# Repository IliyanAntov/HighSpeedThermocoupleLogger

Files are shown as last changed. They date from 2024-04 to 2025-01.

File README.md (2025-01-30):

 <h1 align="center"> Високоскоростен логер за термодвойки с ускорение на измерването<br/><br/>
 High-speed thermocouple logger with measurement acceleration </h1>

## [Документация](./Documentation/DR_Iliyan_Antov_101220020.pdf)

## [Презентация на проекта](./Documentation/Presentation/High%20speed%20thermocouple%20logger.pptx)

## Блокова схема:
<p align="center">
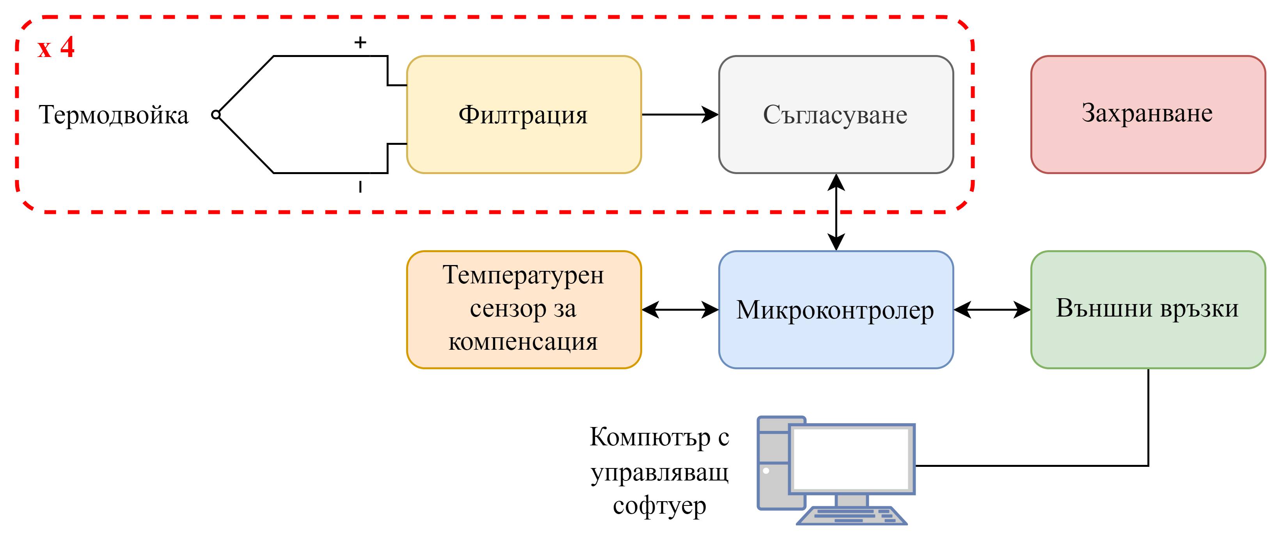
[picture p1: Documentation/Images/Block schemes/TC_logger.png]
  
</p>

## Принципна електрическа схема:
<p align="center" float="left">
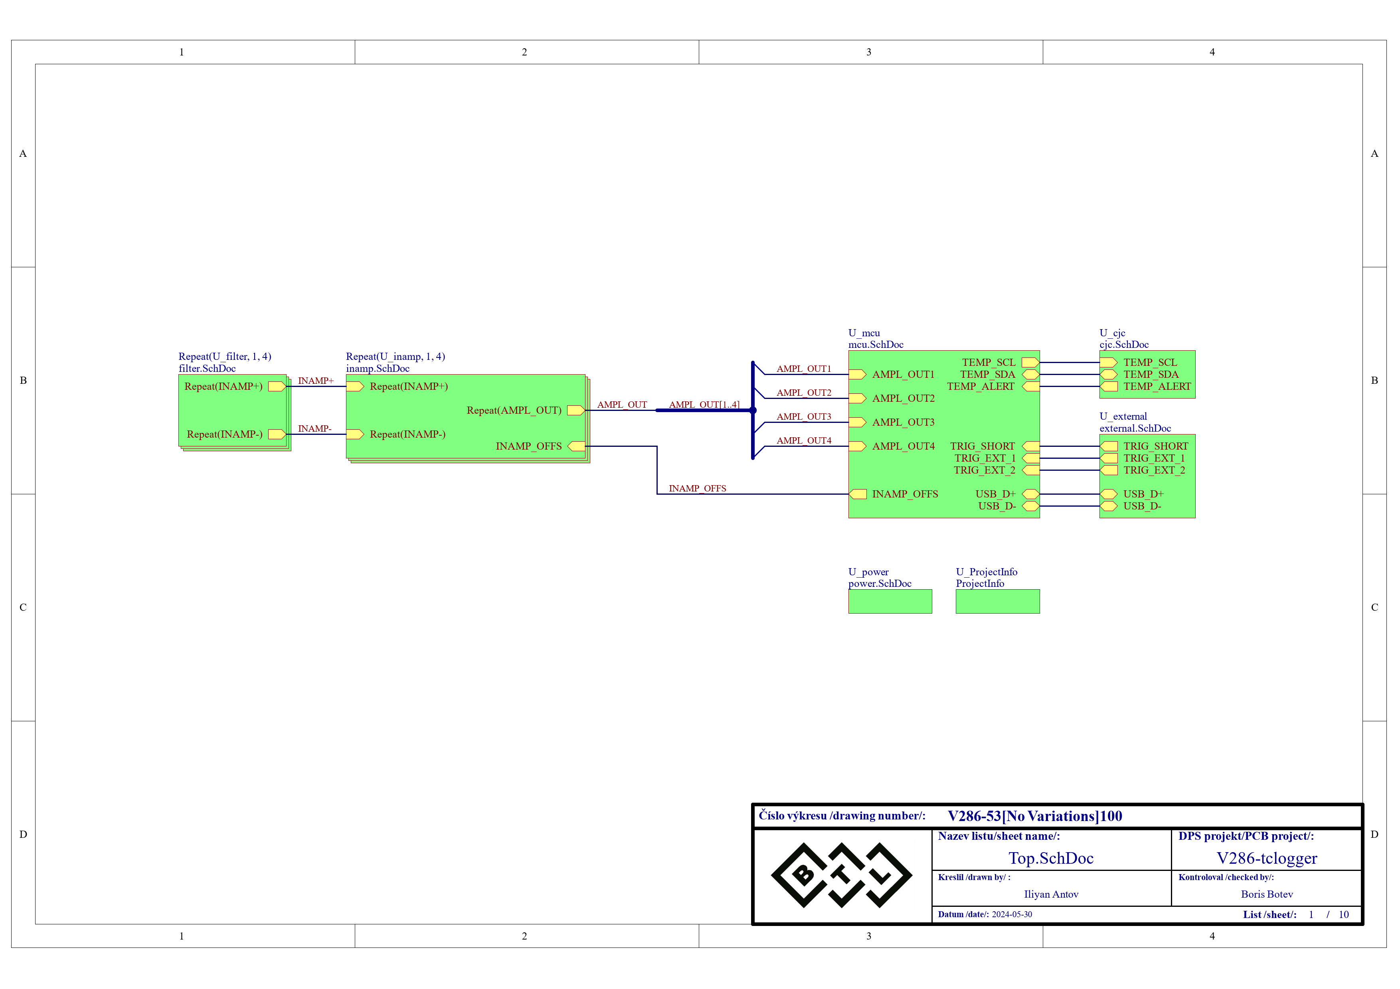
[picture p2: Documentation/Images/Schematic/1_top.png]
  
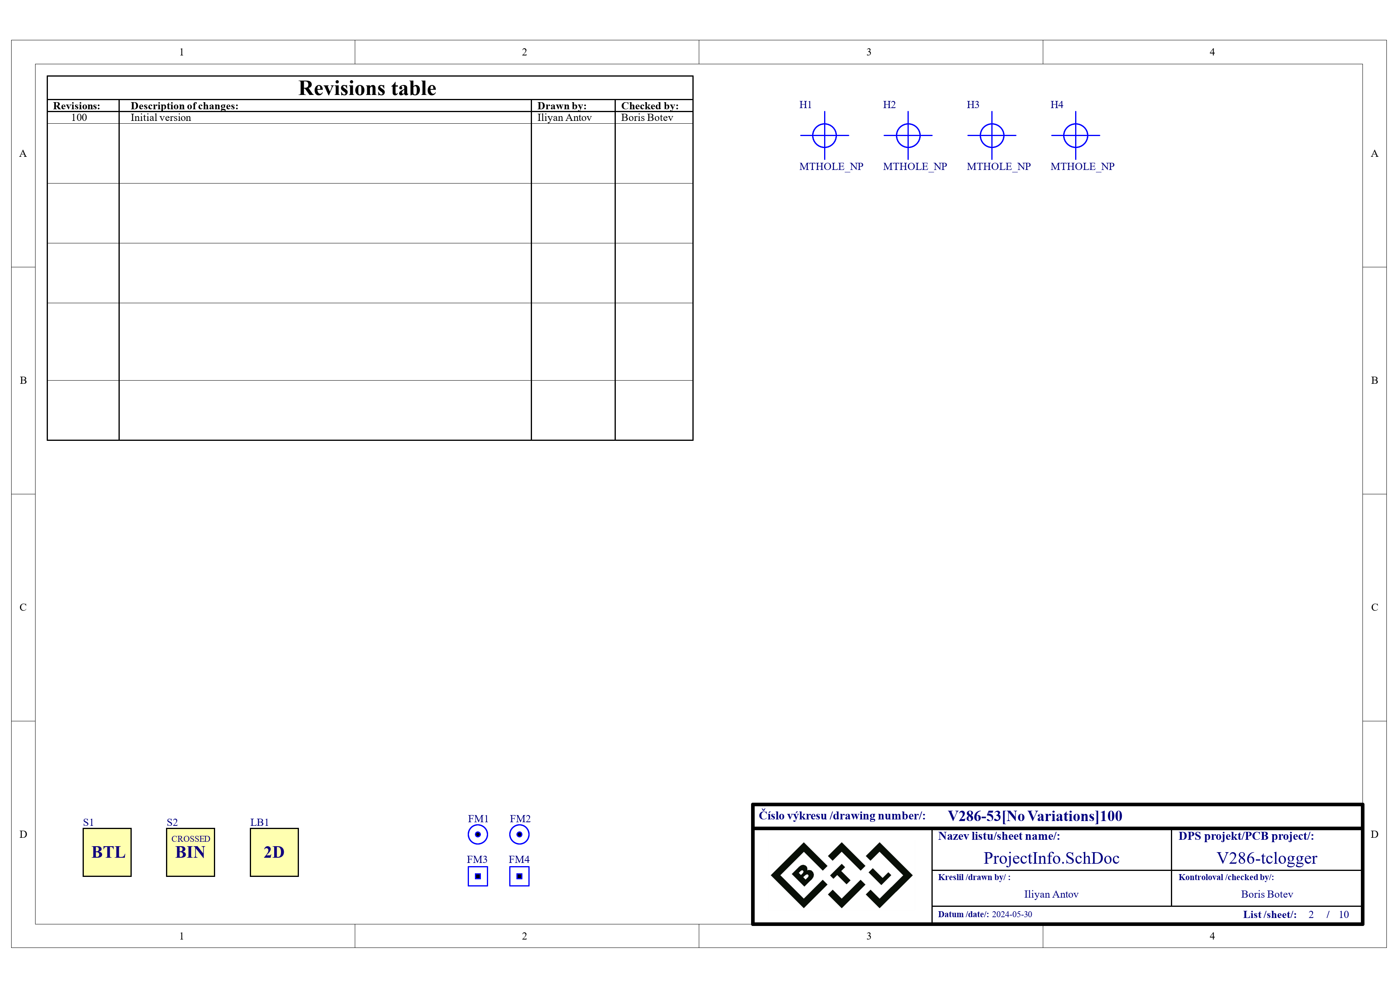
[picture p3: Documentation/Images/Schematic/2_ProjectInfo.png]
  
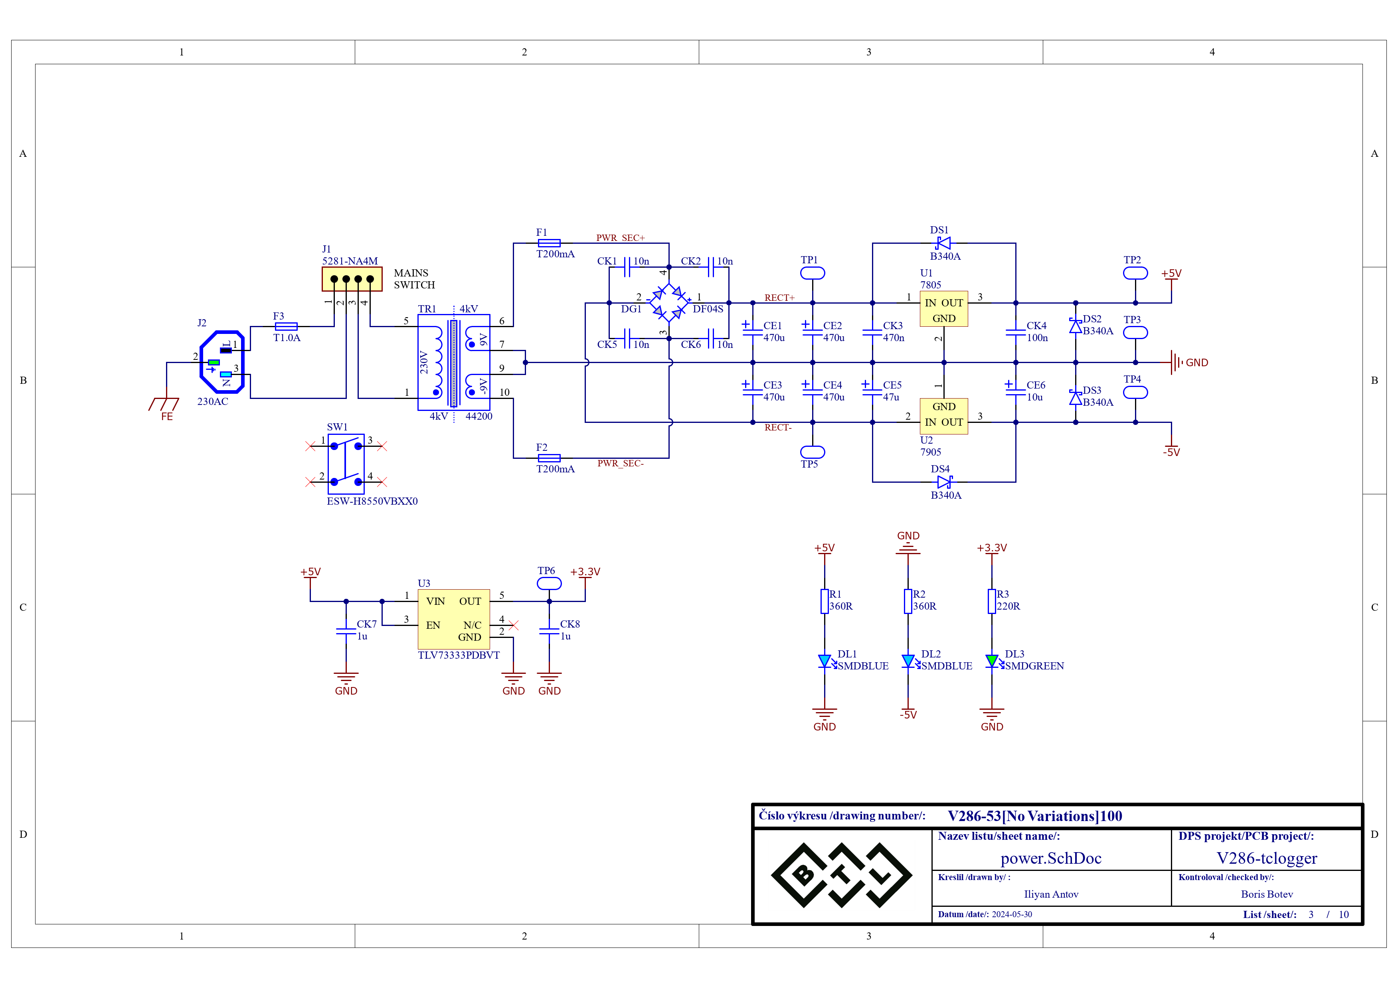
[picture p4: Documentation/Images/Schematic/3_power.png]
  
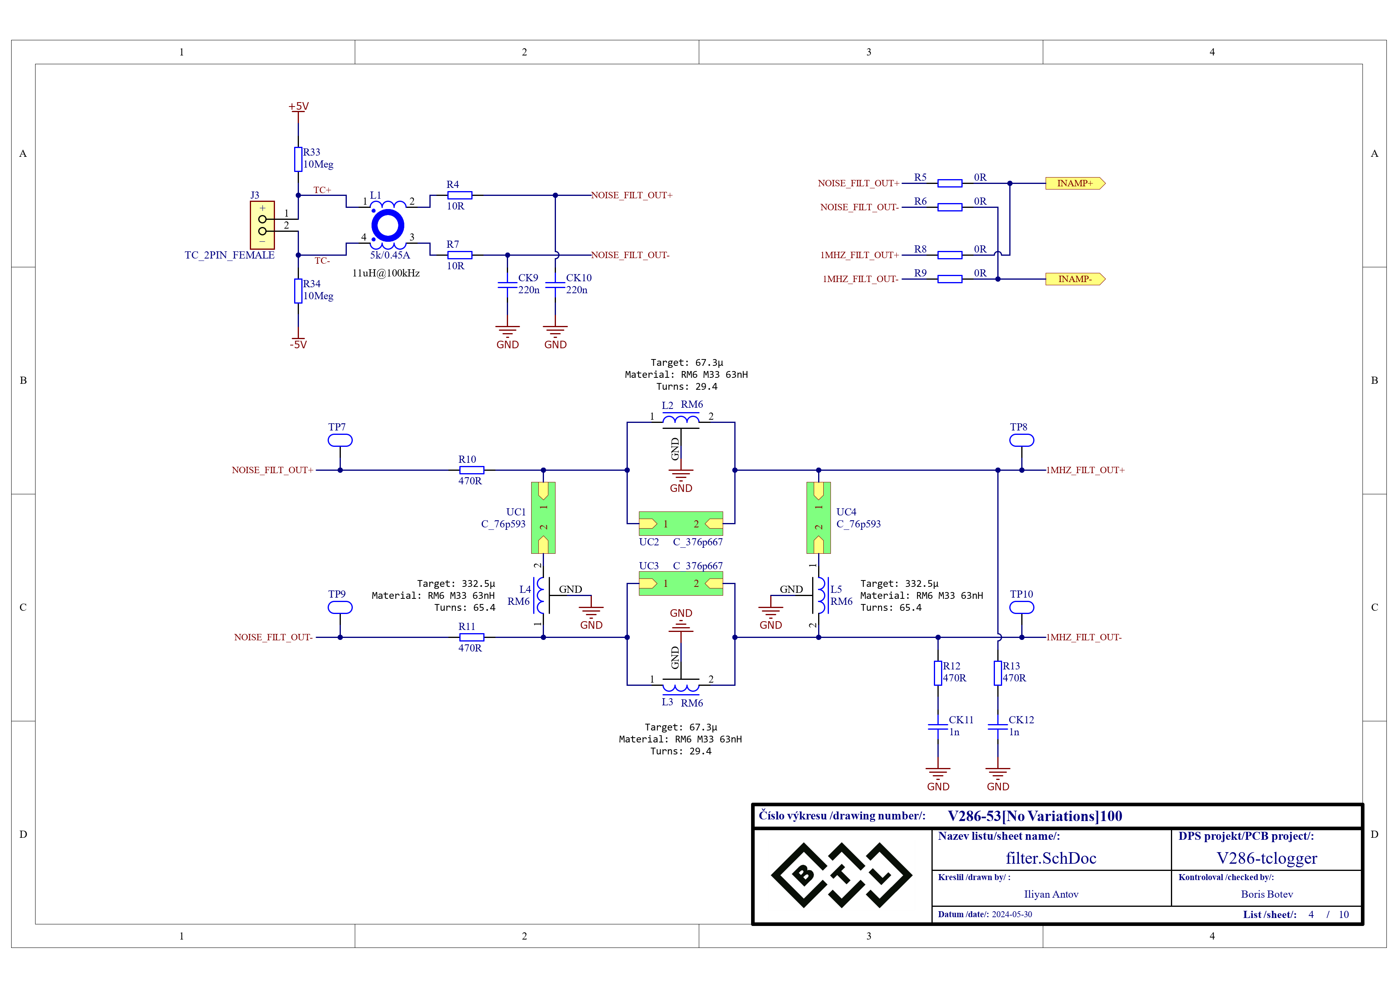
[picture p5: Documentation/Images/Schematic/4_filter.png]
  
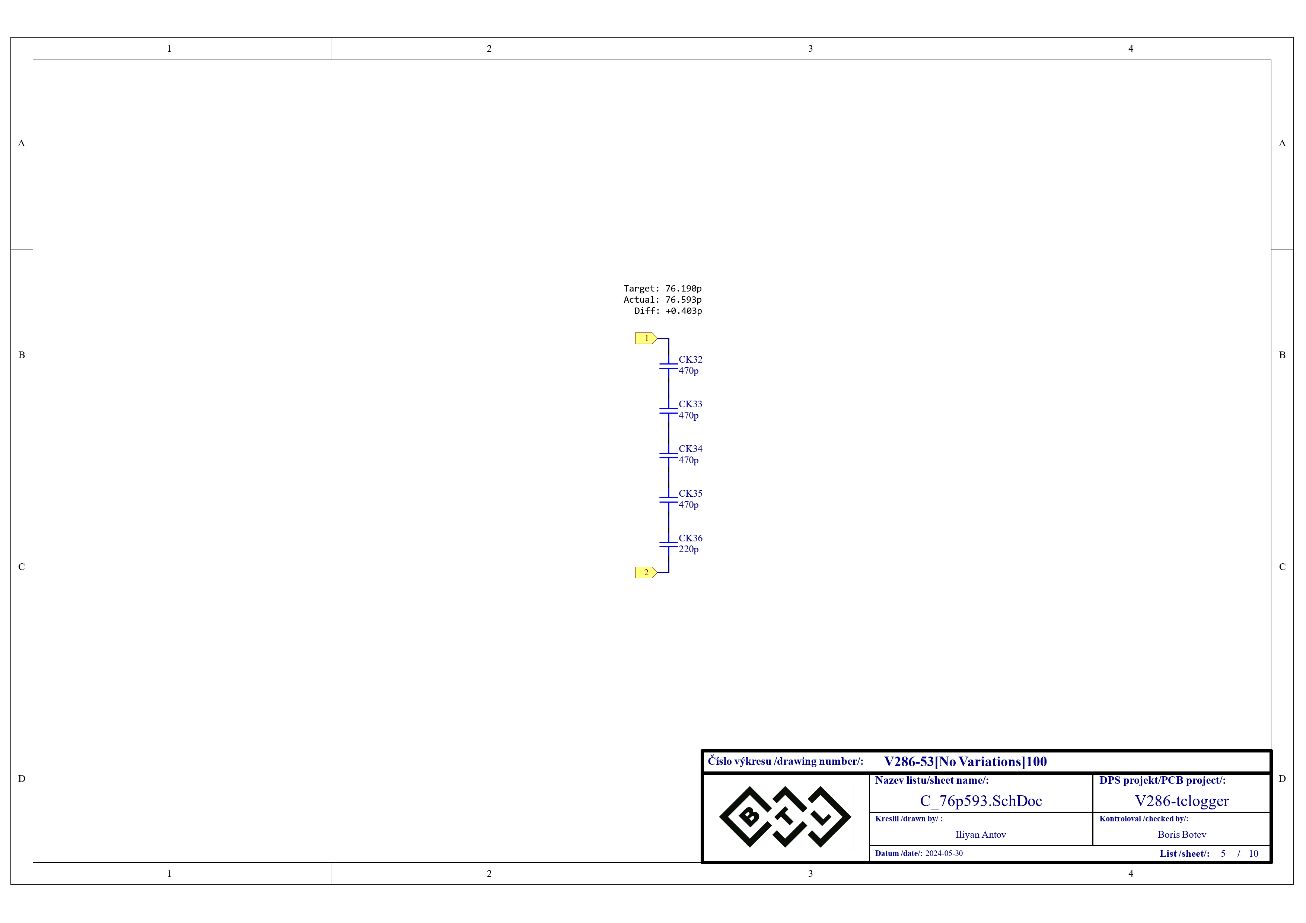
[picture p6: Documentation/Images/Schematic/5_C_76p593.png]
  
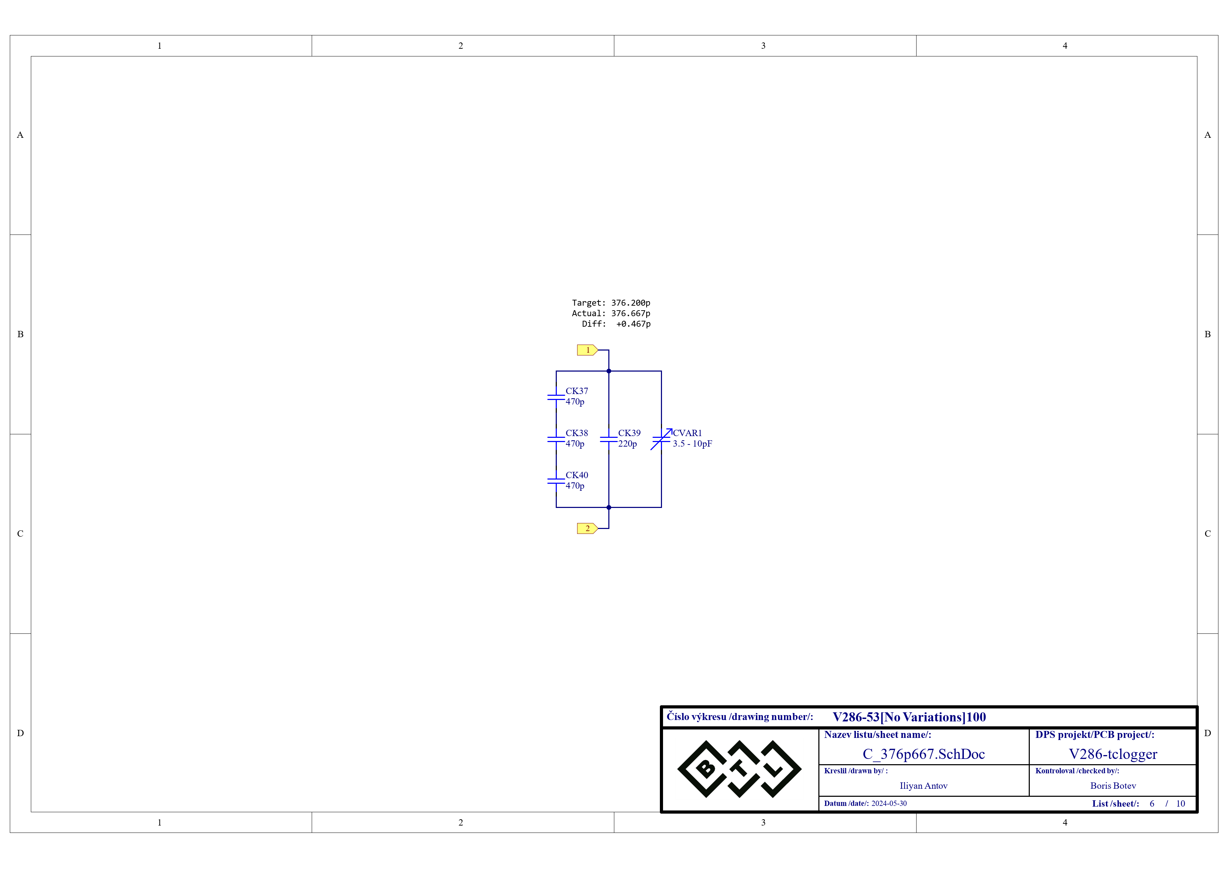
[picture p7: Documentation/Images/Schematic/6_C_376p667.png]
  
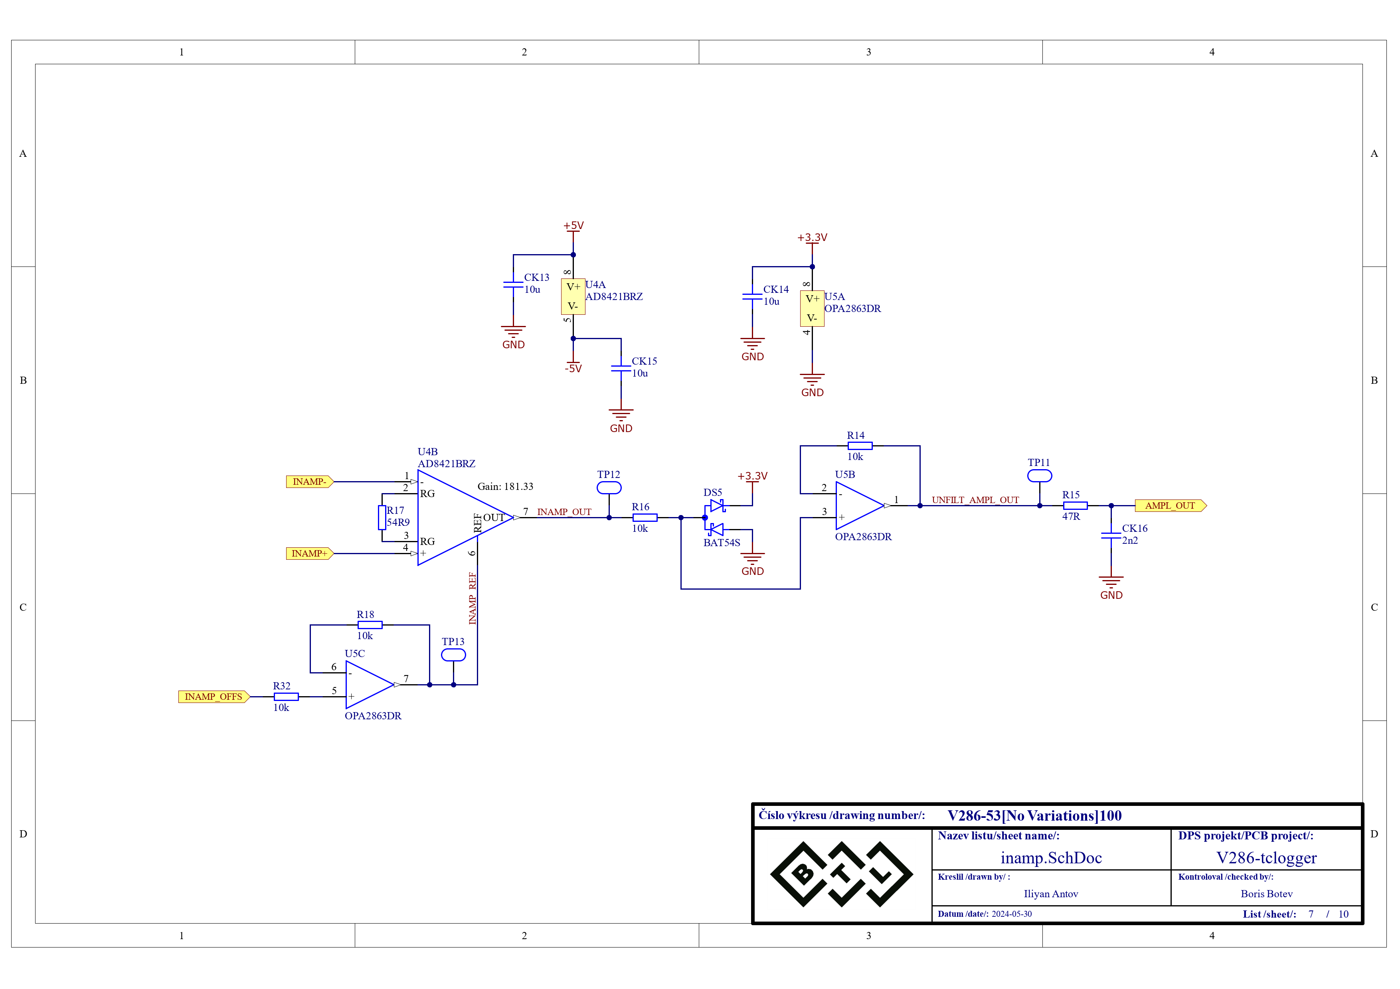
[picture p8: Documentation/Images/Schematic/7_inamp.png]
  
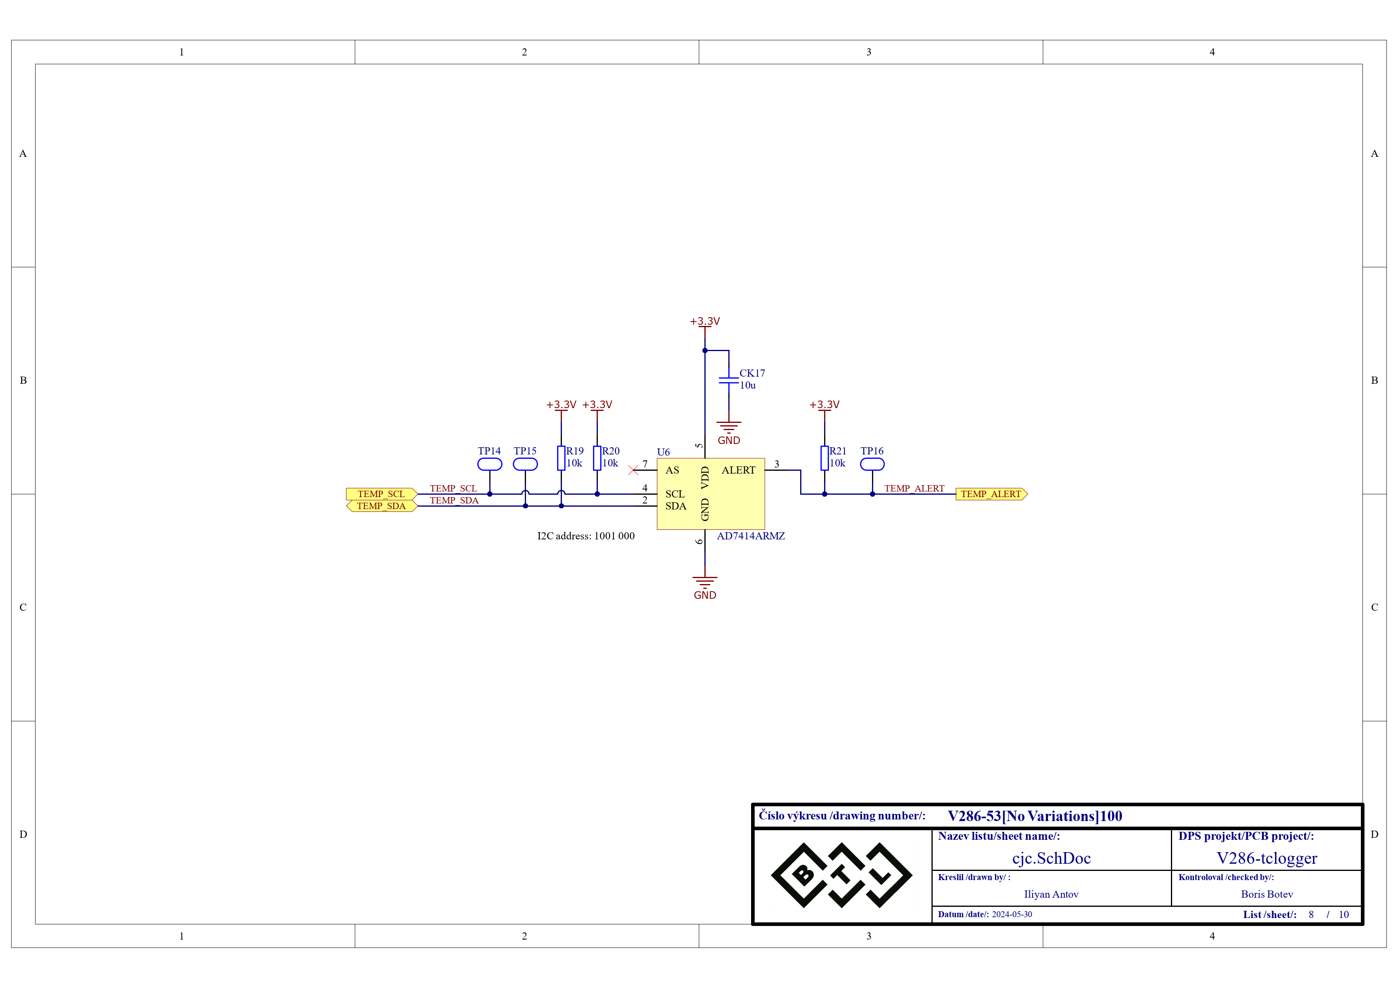
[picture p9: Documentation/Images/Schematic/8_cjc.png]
  
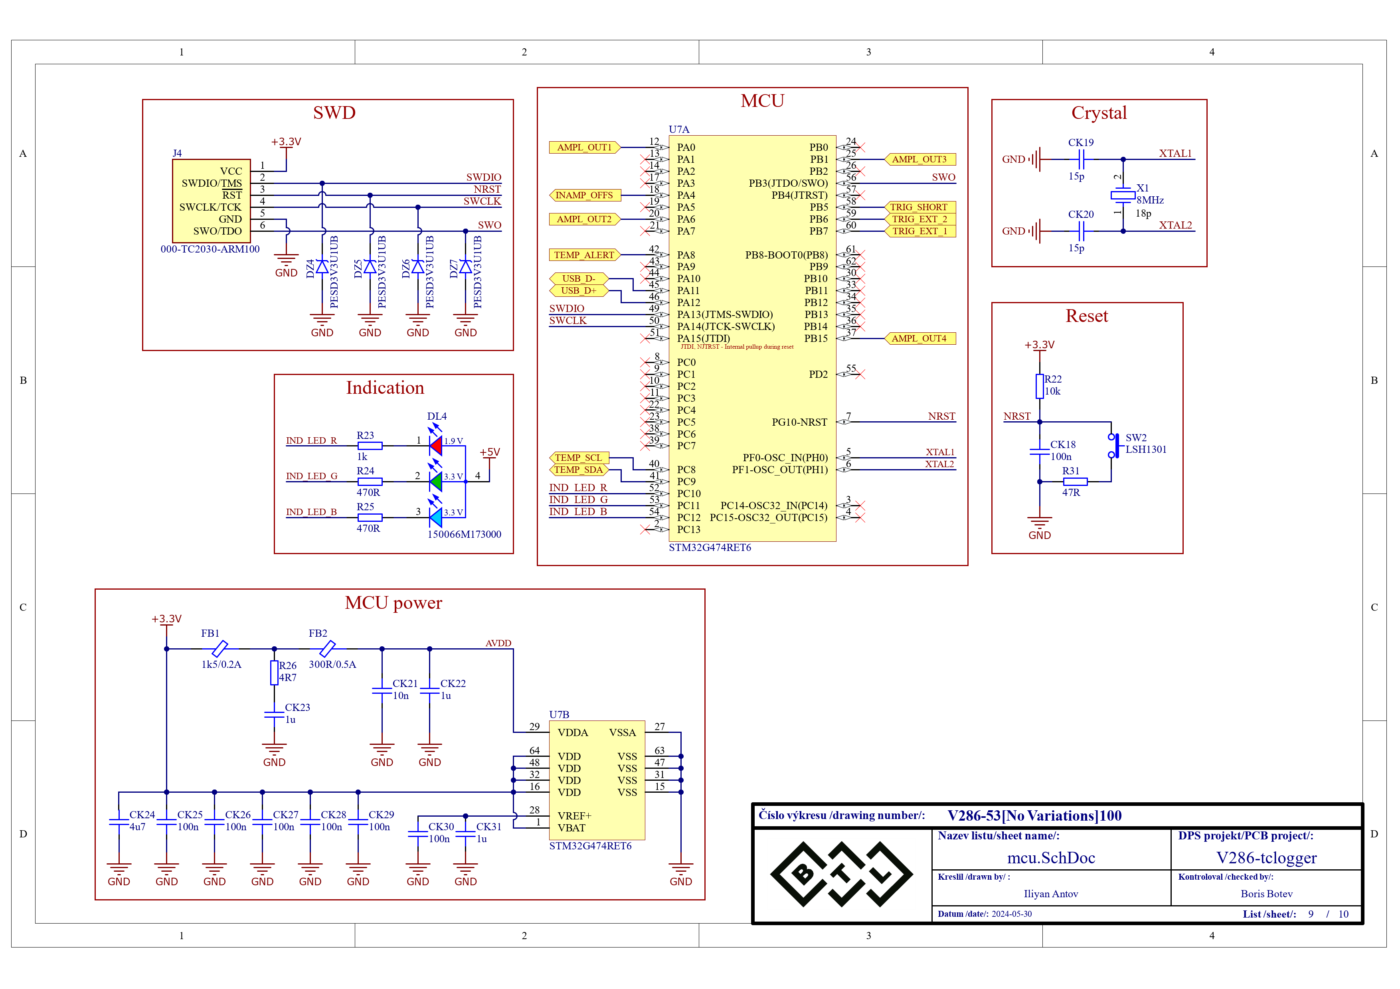
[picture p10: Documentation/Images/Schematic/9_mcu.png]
  
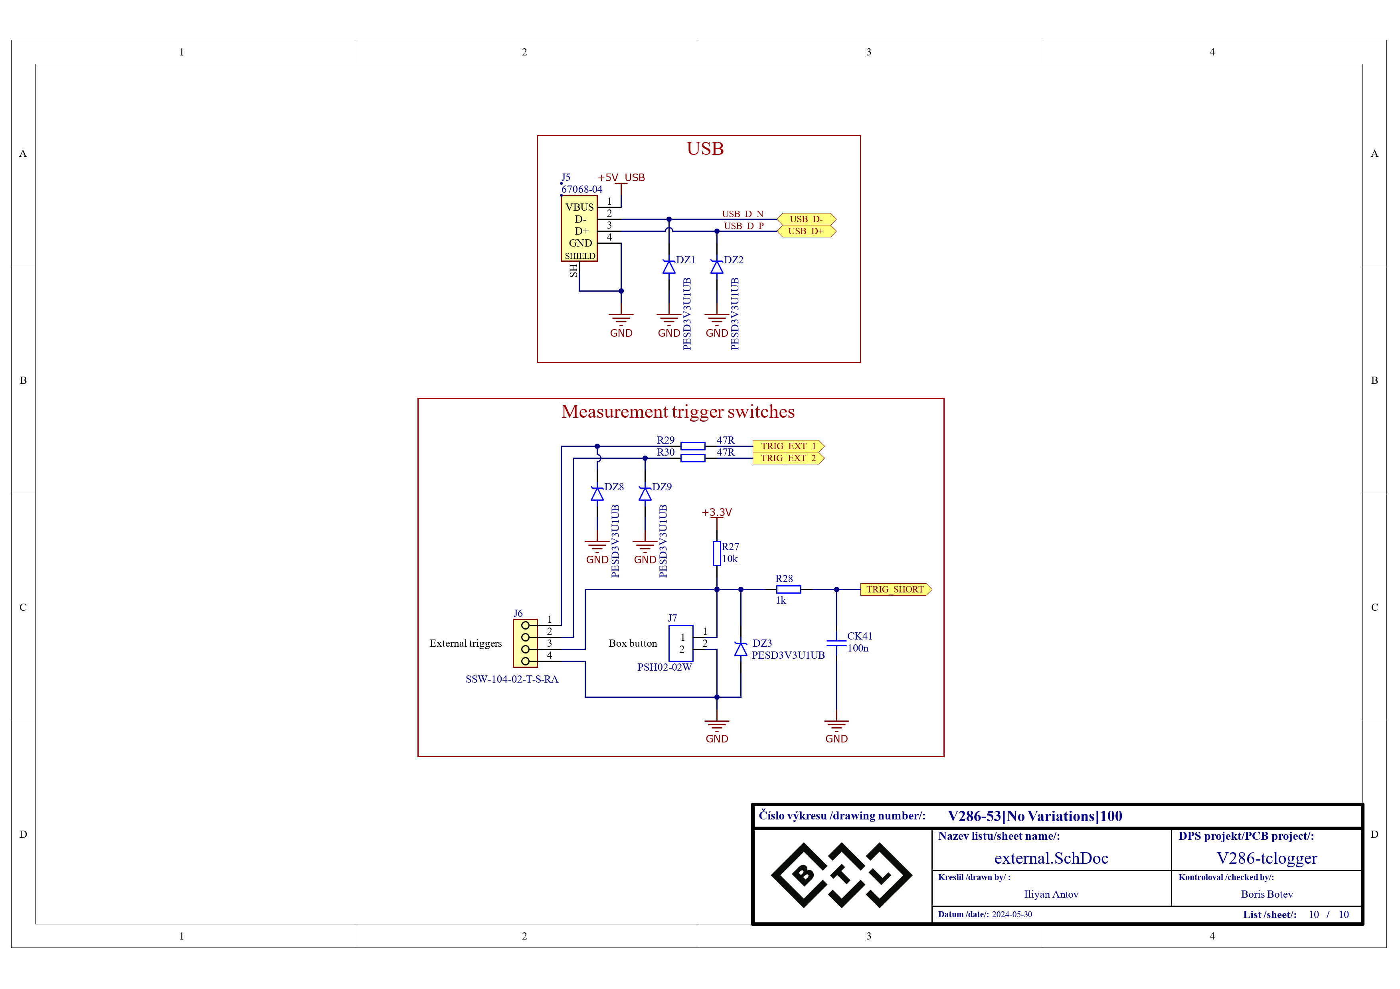
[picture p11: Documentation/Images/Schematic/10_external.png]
  
</p>

## Печатна платка:
<p align="center">
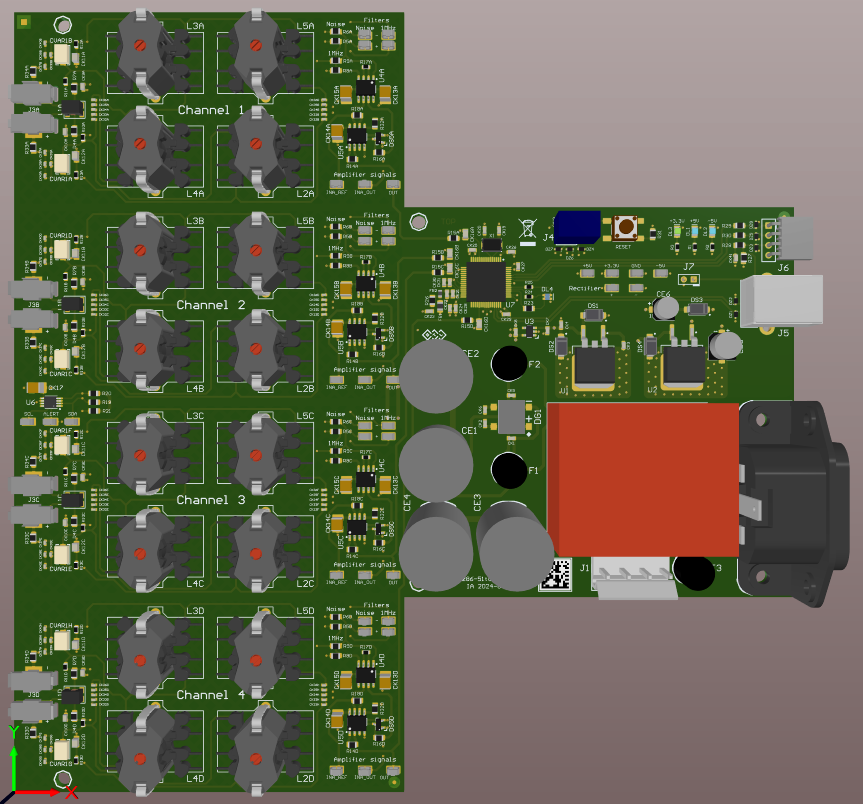
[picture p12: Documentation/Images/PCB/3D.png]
  
</p>

## Реализация:
<p align="center">
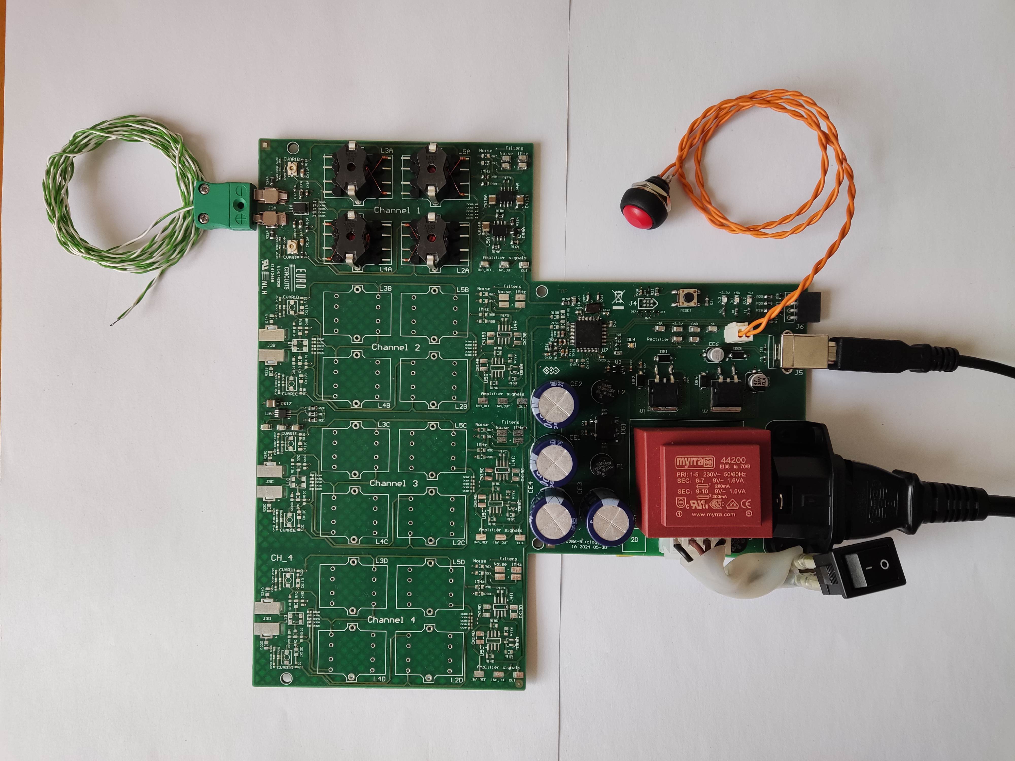
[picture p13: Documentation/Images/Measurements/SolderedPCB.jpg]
  
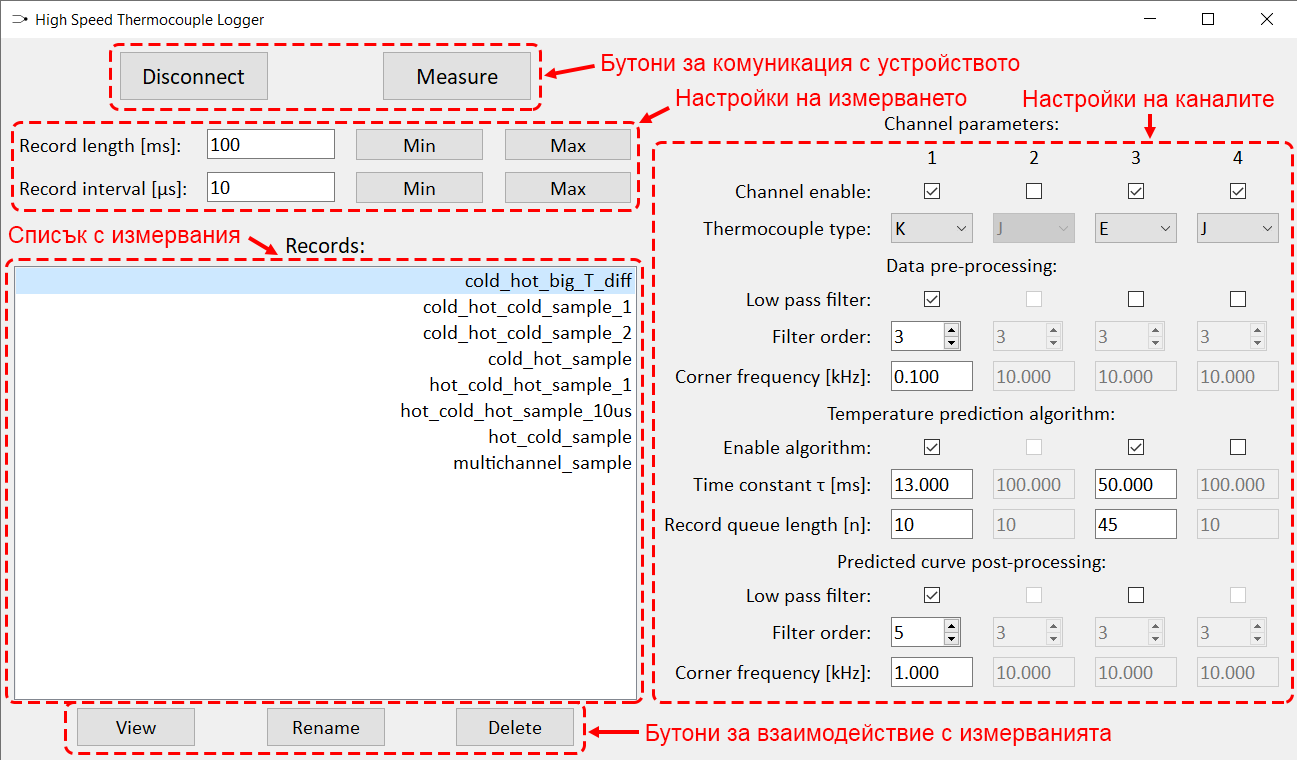
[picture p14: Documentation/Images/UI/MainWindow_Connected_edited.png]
  
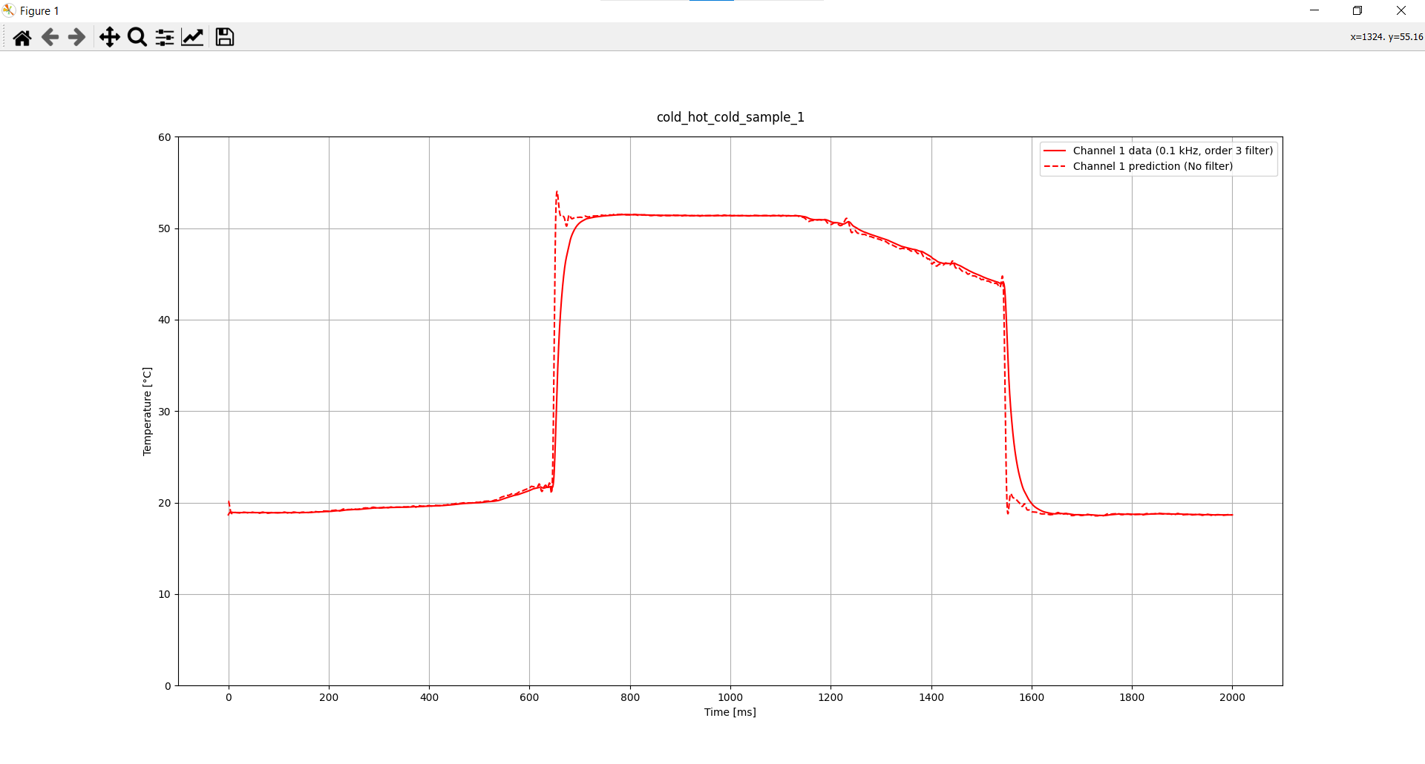
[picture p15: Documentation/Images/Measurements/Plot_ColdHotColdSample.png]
  
</p>

## Използвани технологии:
* PC application: Python + PyQt5
* Firmware: C/C++
* MCU platform: STM32
* Schematics/Layout: Altium

## Автор:
Илиян Антов - [Iliyan Antov](https://github.com/IliyanAntov) - [i.antov2@gmail.com](i.antov2@gmail.com)

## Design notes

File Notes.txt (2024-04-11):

Chosen MCU: STM32G474
Chosen In-amp: AD8421
Chosen temperature range: -20°C to 200°C
Using internal reference voltage buffer of STM32G474

Thermocoule full scale voltages at chosen temperature range:
	J: 11.774 mV 
	K: 8.916 mV
	T: 10.045 mV
	E: 14.573 mV
Maximum TC reverse voltage for chosen temperature range:
	J: -0.995 mV 
	K: -0.778 mV
	T: -0.757 mV
	E: -1.152 mV

Using Vtc(max) = 14.573  mV for further calculations

Vref+ and Vref- requirements for STM32G474:
	Vref- == Vssa 		tied internally
	Vref+ == Vdda 		when Vdda < 2V
	2V < Vref+ < Vdda 	when Vdda >= 2V

Vdda and Vssa requirements for STM32G474:
	1.62V < Vdda < 3.6V
	When Vrefbuf_out = 2.9V is used: 3.135V < Vdda < 3.6V
	Vssa = Vss = 0V

Choose Vdda = Vdd = 3.3V
Total amplification needed: Au = Vref+(max) / Vtc(fs) = 2.9/14.573m = 199 times ~= 46dB

Choose in-amp with Au = 199.4

Available internal reference voltages for STM32G474: 
	VRS=00 => Vrefbuf_out = 2.048V +- 4mV
	VRS=01 => Vrefbuf_out = 2.5V +- 4mV
	VRS=10 => Vrefbuf_out = 2.9V +- 4mV

Chosen Vrefbuf_out for each thermocouple type where Vref+ <= (Vtc(fs) * Au):
	J: 2.348V => Vref+ = 2.5V 
	K: 1.778V => Vref+ = 2.048V 
	T: 2.003V => Vref+ = 2.048V 
	E: 2.906V => Vref+ = 2.9V 

-----------------------------------------------------------------------------

Power supplies needed:
In-amp:
	+Vs: +5V
	-Vs: -5V
	REF: 1.152mV
MCU:
	VDD/AVDD: +3.3V
	VSS/AVSS: 0V

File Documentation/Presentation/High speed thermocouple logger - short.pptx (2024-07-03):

## Регистриране на високоскоростен температурен процес

ФЕТТ, BTL Industries
Илиян Антов
2024

## Задача

## Радиочестотен микронидлинг

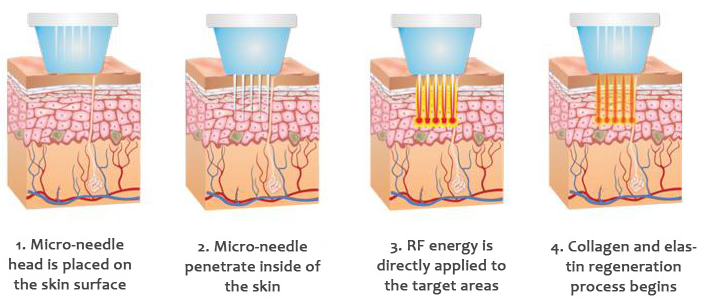
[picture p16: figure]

## Ефект на температурата върху тъканта

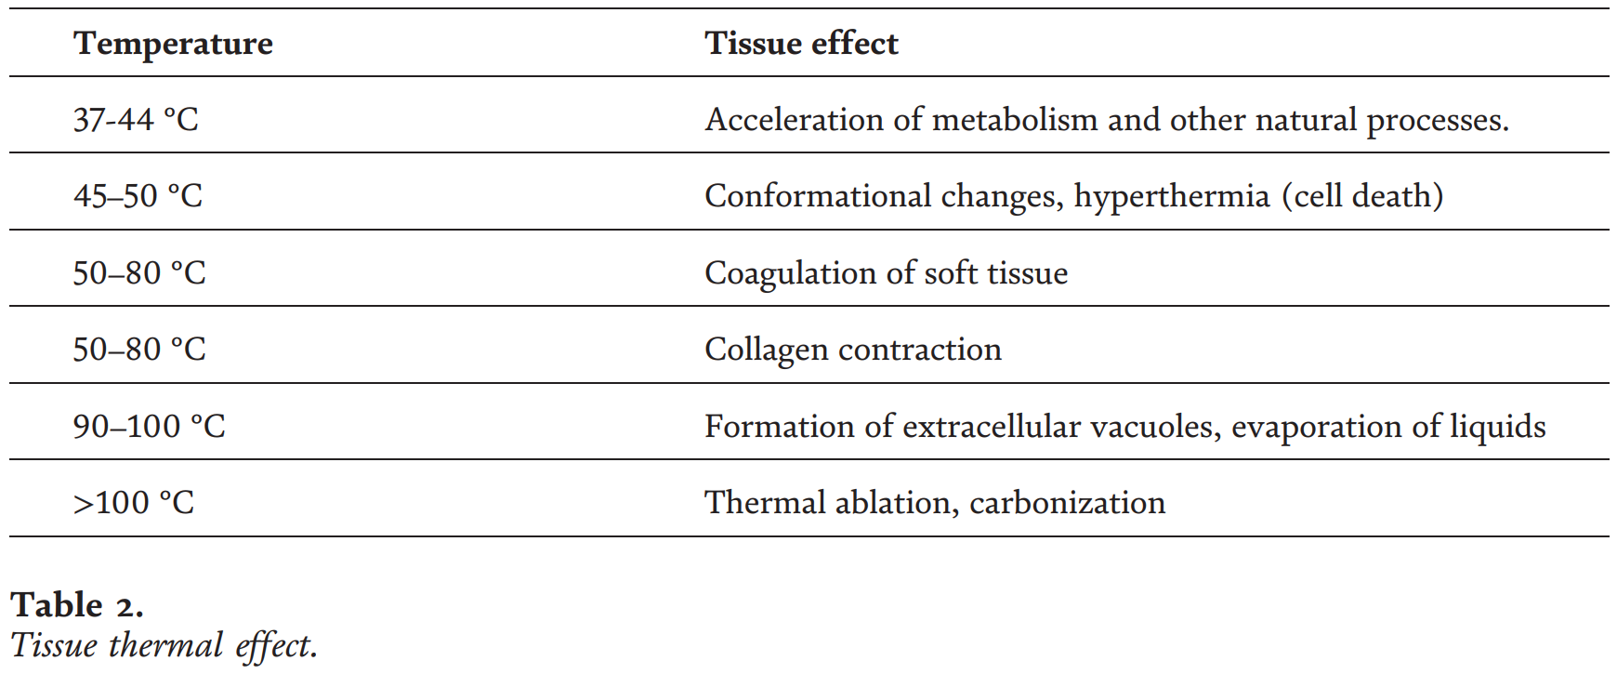
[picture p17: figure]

## Текущ метод за контрол на процеса

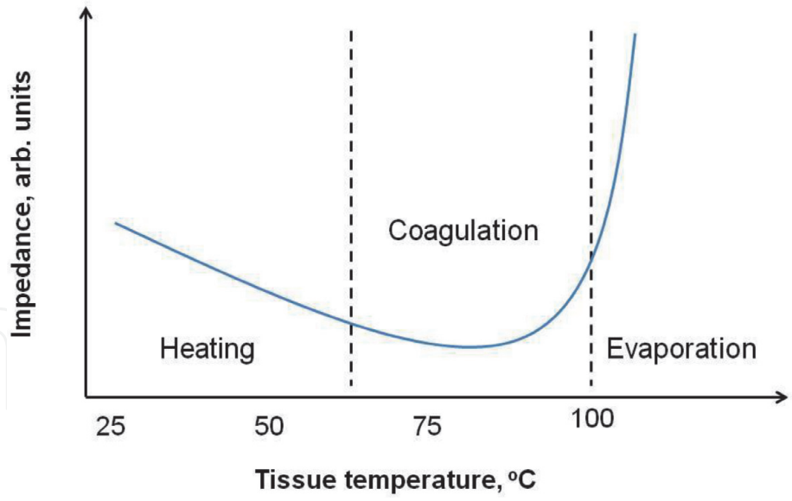
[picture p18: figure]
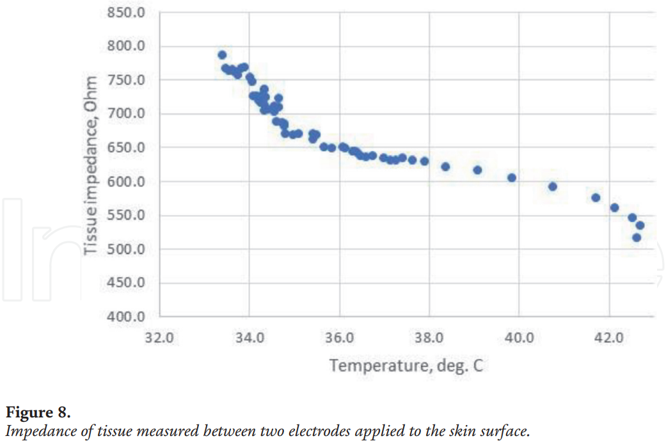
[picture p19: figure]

## 2. Избор на решение

## Проблеми със съществуващите решения

- Бавно семплиране - обикновено до няколко Hz
- Висока цена
- Липса на филтрация на входовете
- Частично решение - неизгодно

## Избор на температурен сензор

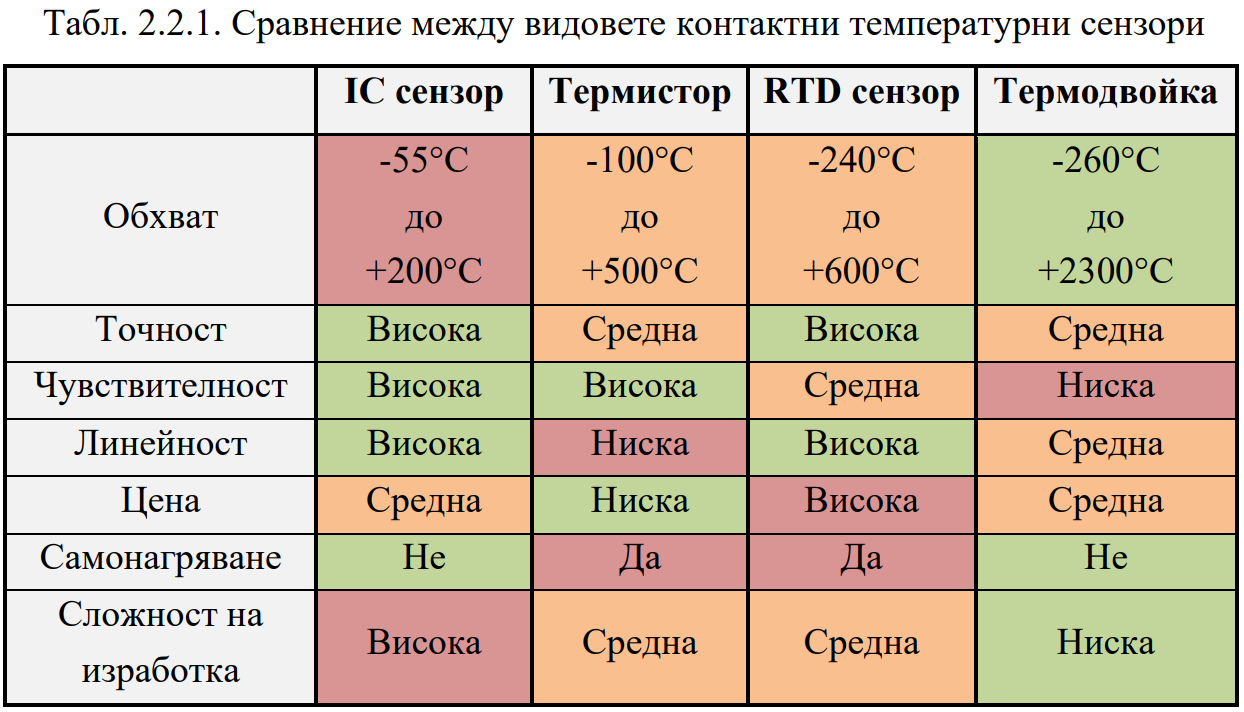
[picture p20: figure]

## Коаксиални термодвойки

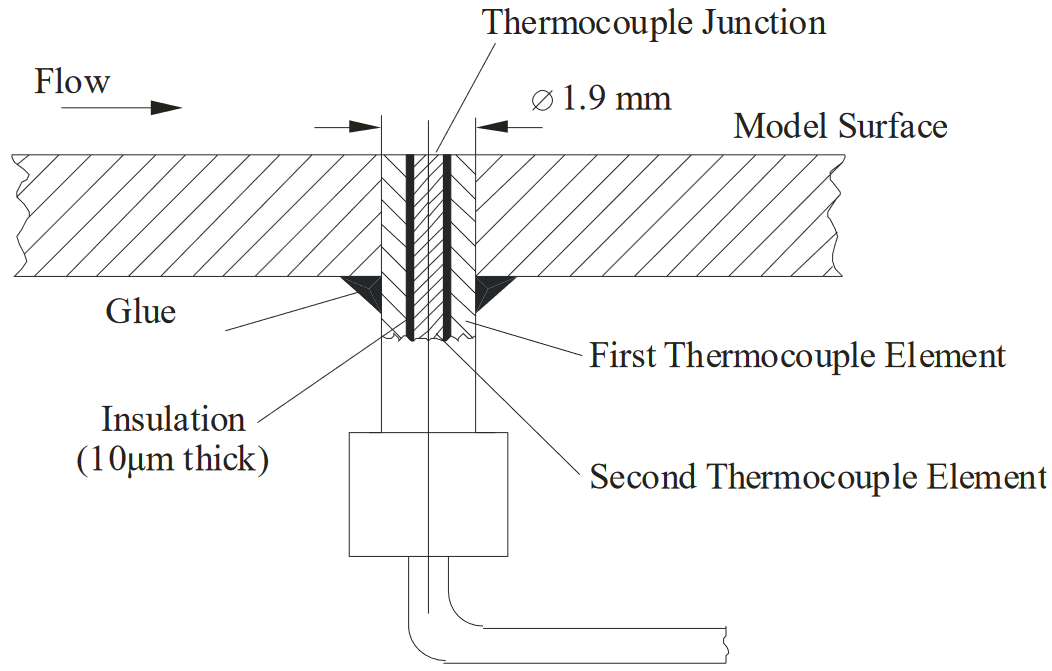
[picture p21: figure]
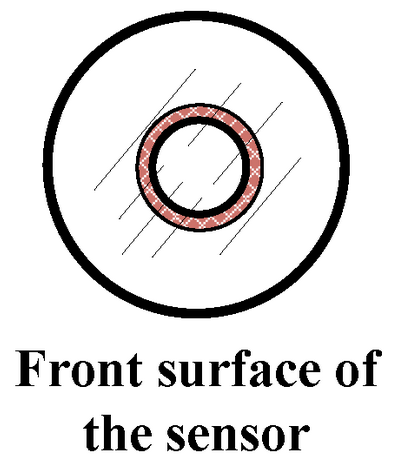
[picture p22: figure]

## 3. Проектиране

## Блокова схема

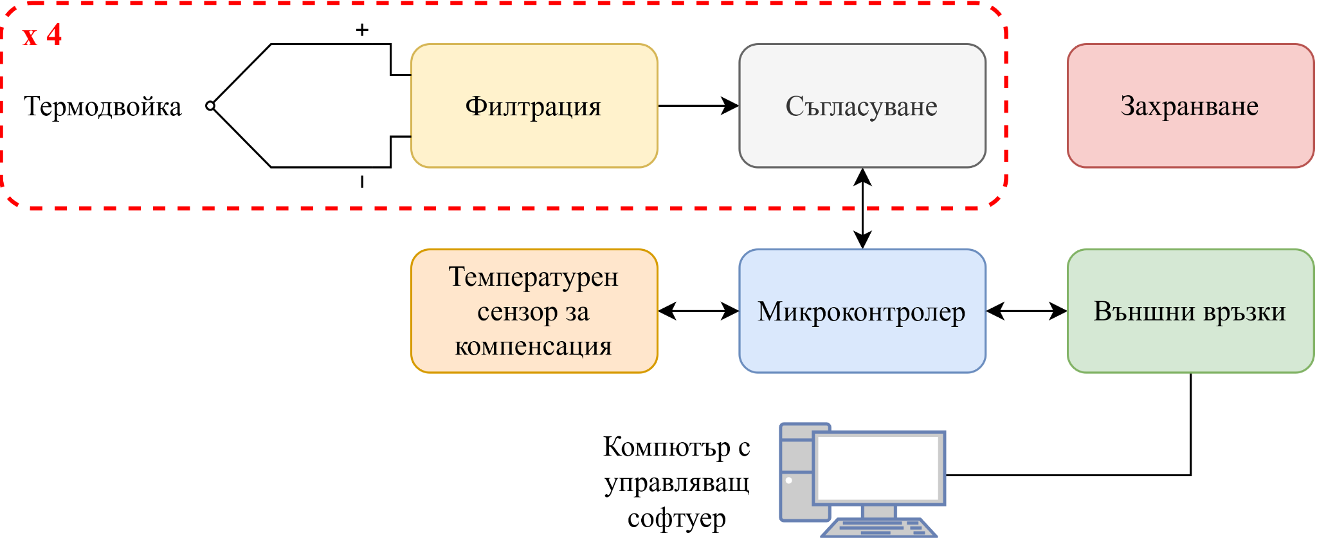
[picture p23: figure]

## Принципна електрическа схема

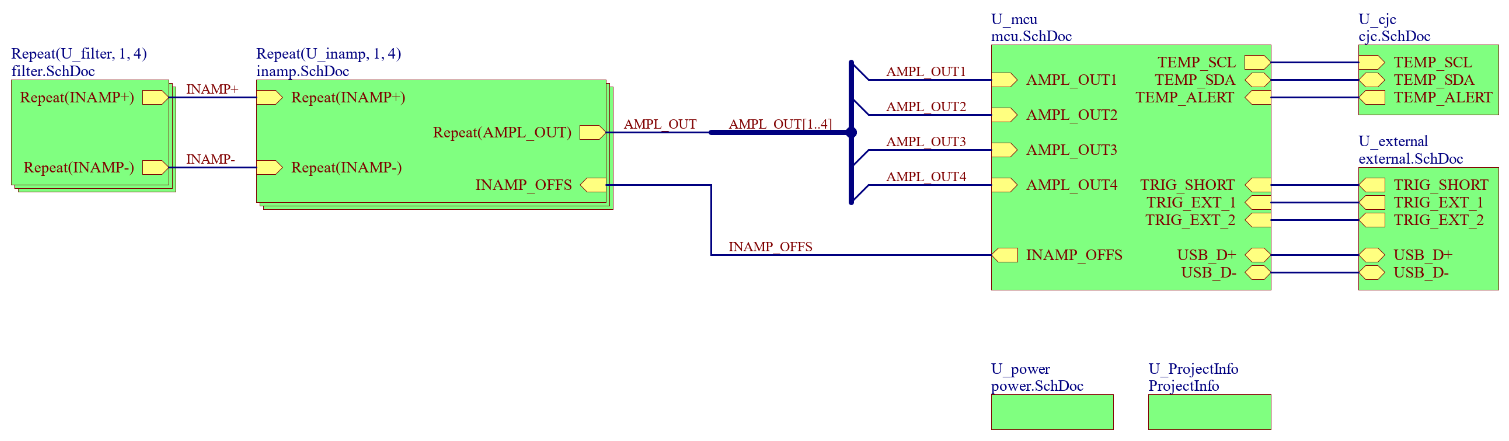
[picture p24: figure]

## Комуникационен протокол

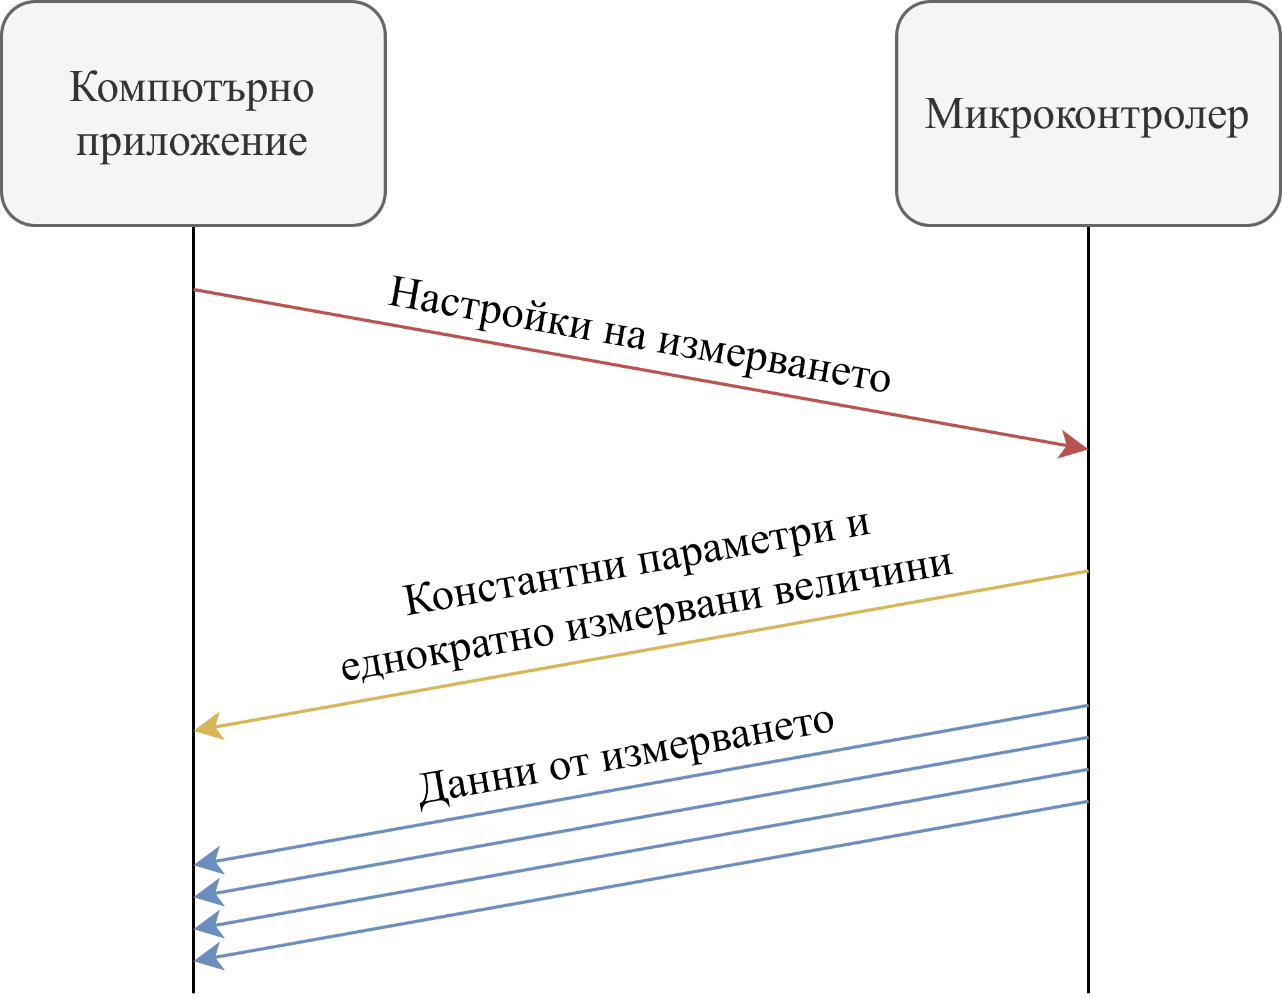
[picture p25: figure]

## Компютърно приложение - Главен прозорец


## Компютърно приложение - Прозорец за преглед на измерване

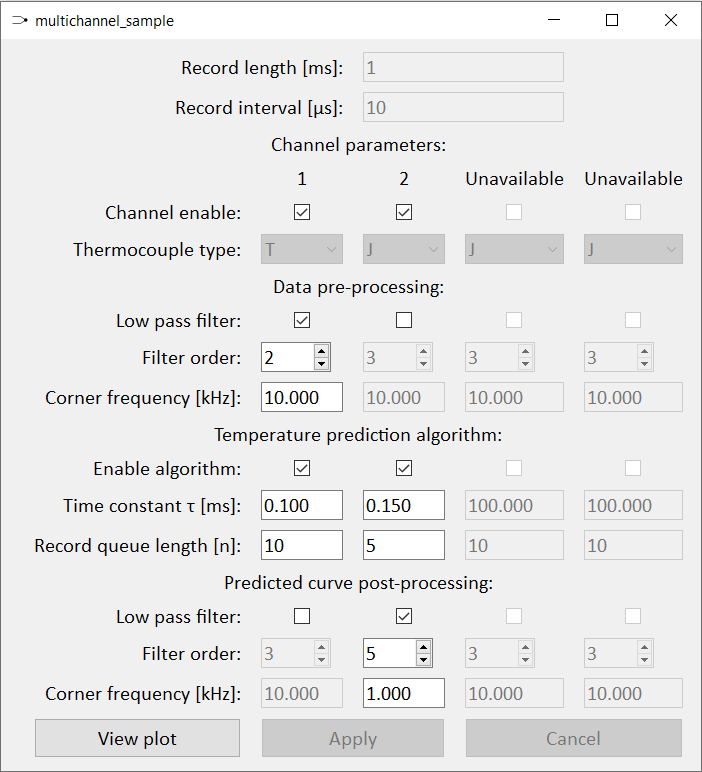
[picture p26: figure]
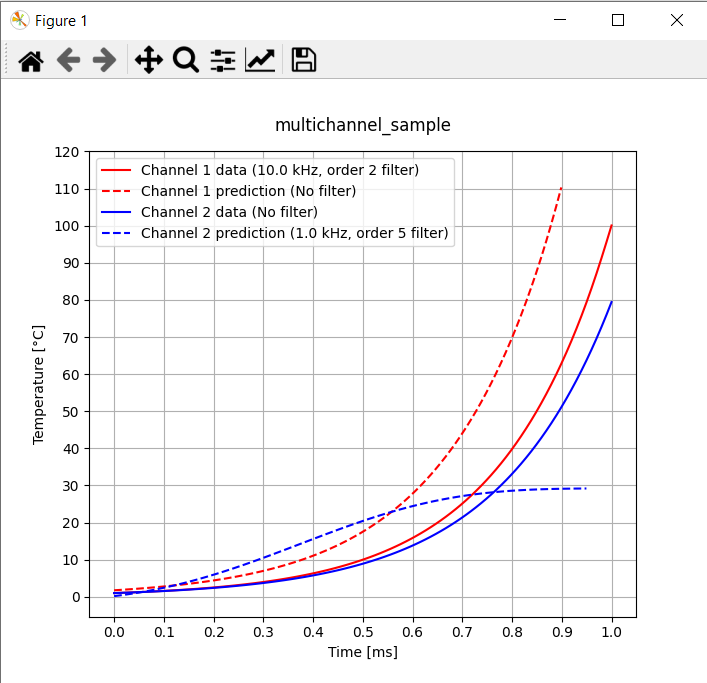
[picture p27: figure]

## Компютърно приложение - Предвиждане на температурата

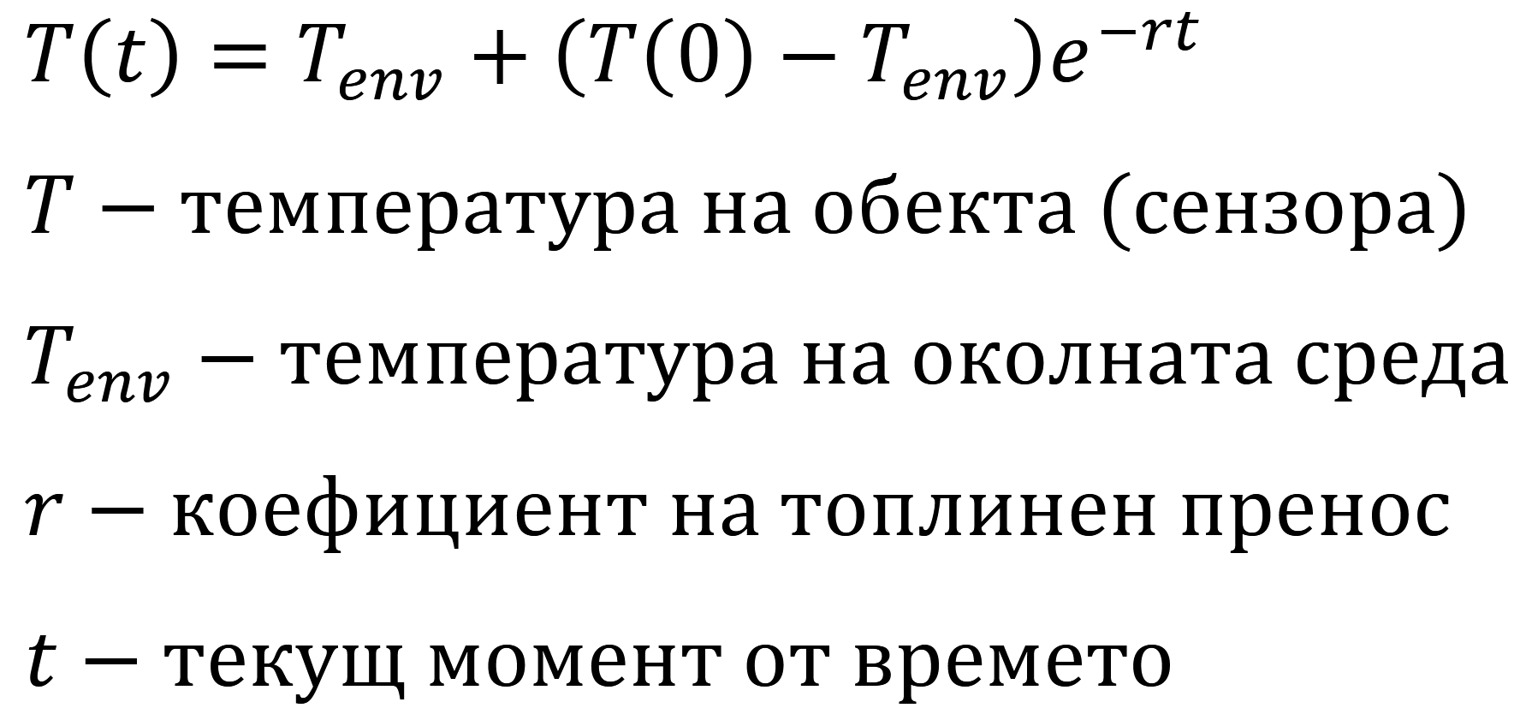
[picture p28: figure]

## Печатна платка


## 4. Резултати

## Наситена печатна платка

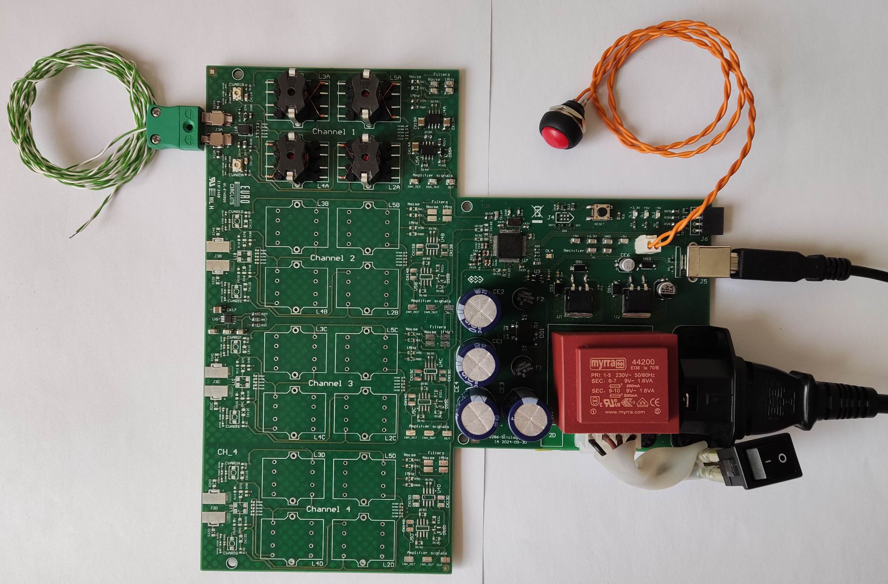
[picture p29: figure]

## Експеримент студено-топло-студено


## Експеримент студено-топло, фронт

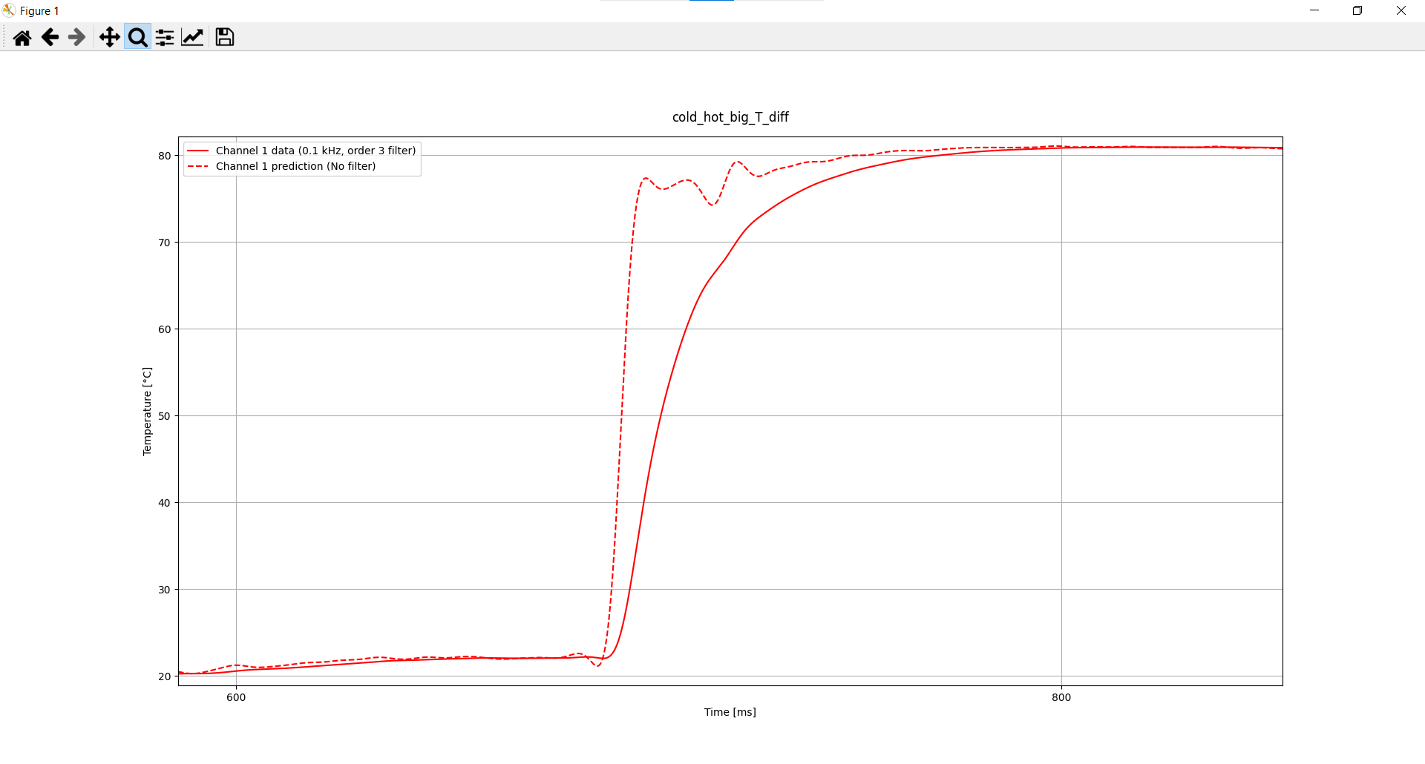
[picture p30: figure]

## Демонстрация

## Въпроси?

## Благодаря!

## Използвани източници

[1] The Basic Science of Radiofrequency-Based Devices – Michael Kreindel and Stephen Mulholland (https://inmodemd.com/wp-content/uploads/2021/03/PeerRev_IntechChapter_RFScience_MKSM.pdf)
[2] Comparing Contact and Non-Contact Temperature Sensors – Process Parameters (https://www.processparameters.co.uk/comparing-contact-and-non-contact-temperature-sensors/)
[3] Comparing Contact and Non-Contact Temperature Sensors – AZo Sensors (https://www.azosensors.com/article.aspx?ArticleID=2347)
[4] Thin Film Gauges and Coaxial Thermocouples for Measuring Transient Temperatures - Müller Instruments (https://mueller-instruments.de/fileadmin/Downloads/englische_medien/Description-gauges.pdf)
[5] Newton's law of cooling - Wikipedia (https://en.wikipedia.org/wiki/Newton%27s_law_of_cooling)

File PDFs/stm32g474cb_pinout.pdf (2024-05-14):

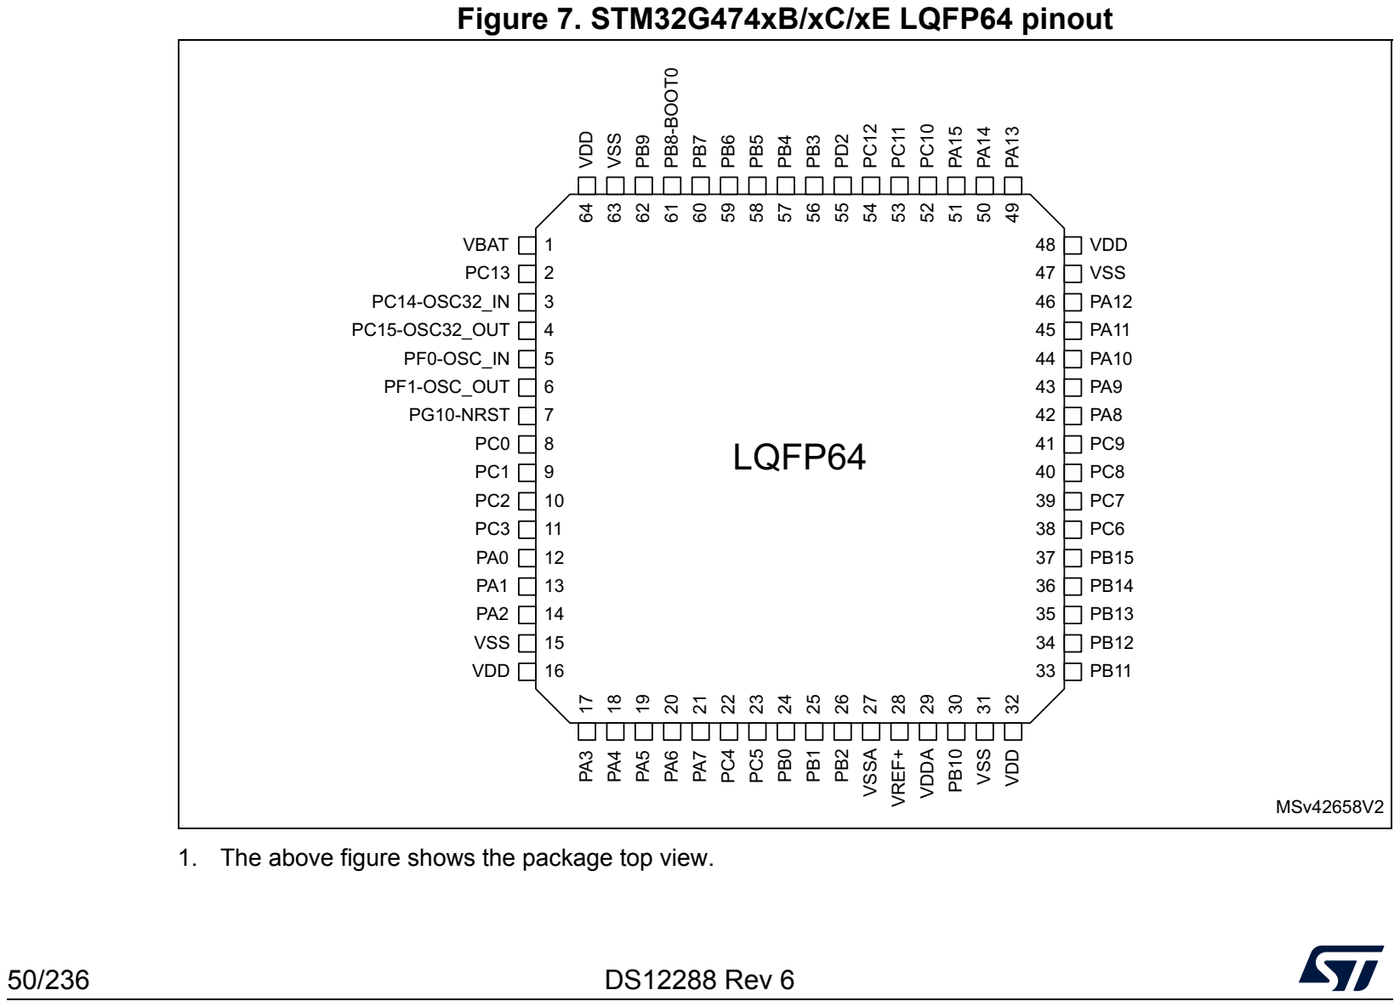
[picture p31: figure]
DS12288 Rev 6; MSv42658V2; LQFP64; VBAT; PC14-OSC32_IN; PC15-OSC32_OUT; PF0-OSC_IN; PF1-OSC_OUT; PG10-NRST; VSS; VDD; VREF+; VSSA; VDDA; PB8-BOOT0

## Figure 7. STM32G474xB/xC/xE LQFP64 pinout

1. The above figure shows the package top view.

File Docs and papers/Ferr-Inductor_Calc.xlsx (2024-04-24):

Input Coils | RM5 | RM6 | RM6 | RM6 | RM6 | RM6
Material | K1 | K1 | M33 63 | M33 63 | K1 | K1
L (input) |  |  | 0.0003325 | 6.73e-05
AL min | 4e-08 | 4e-08 | 6.3e-08 | 6.3e-08 | 4e-08 | 4e-08
k AL | 2 | 2 | 2 | 2 | 2 | 2
AL max | 8e-08 | 8e-08 | 1.26e-07 | 1.26e-07 | 8e-08 | 8e-08
AL average | 6e-08 | 6e-08 | 9.45e-08 | 9.45e-08 | 6e-08 | 6e-08
Ae mm2 | 11 | 15 | 15 | 15 | 15 | 15
Turns/mm | 0.00 | 0.00 | 1.99 | 1.33 | 0.00 | 0.00
Max D wire | 0.5 | 0.5 | 0.5 | 0.5 | 0.33 | 0.33
Max turns possible | 44 | 60 | 60 | 60 | 137.7410468 | 137.7410468
N (result) | 0.0 | 0.0 | 59.3 | 26.7 | 0.0 | 0.0

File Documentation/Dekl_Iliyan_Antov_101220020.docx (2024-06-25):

ДЕКЛАРАЦИЯ

Долуподписаният: .................................................................................... , декларирам, че съм разработил самостоятелно представената работа. Не съм използвал източници или ресурси, освен посочените. Ясно съм обозначил използваните източници, които са цитирани буквално или по съдържание.

Декларирам и че работата не е представяна в рамките на друга дипломна защита.

Дата: Подпис: ............................................

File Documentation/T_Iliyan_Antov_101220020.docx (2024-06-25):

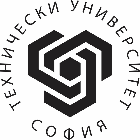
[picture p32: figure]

| Т Е Х Н И Ч Е С К И У Н И В Е Р С И Т Е Т – С О Ф И Я
| | ФАКУЛТЕТ ПО ЕЛЕКТРОННА ТЕХНИКА И ТЕХНОЛОГИИ

#### ДИПЛОМНА РАБОТА

ТЕМА: | РЕГИСТРИРАНЕ НА ВИСОКОСКОРОСТЕН ТЕМПЕРАТУРЕН ПРОЦЕС

ДИПЛОМАНТ: | Илиян Илиянов Антов

РЪКОВОДИТЕЛ: | ас. инж. Николай Тюлиев

София, 2024

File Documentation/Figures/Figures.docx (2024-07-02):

## Параметри (характеристики)

Изисквания към устройството:

- Брой канали: 4
- Температурни сензори: термодвойки от тип J, K, T или E;
- Обхват: -20°C до 200°C
- Чувствителност: 1°C;
- Честота на семплиране: до 100 kS/s (100 kHz), т.е. период на семплиране 10 μs;
- Връзка към компютър: посредством USB интерфейс;
- Управление: чрез компютърно приложение;
- Възможност за вторична обработка на измерванията с цел ускоряване на измерването и допълнителна филтрация;
- Филтрация на случайни синфазни и диференциални шумове за всеки от каналите;
- Възможност за включване на специална дълбока филтрация към всеки от каналите, предназначена за потискане на синфазен и диференциален шум с честота 1 MHz, породен от загряващия RF ток;
- Възможност за визуализация и записване на снетите данни.

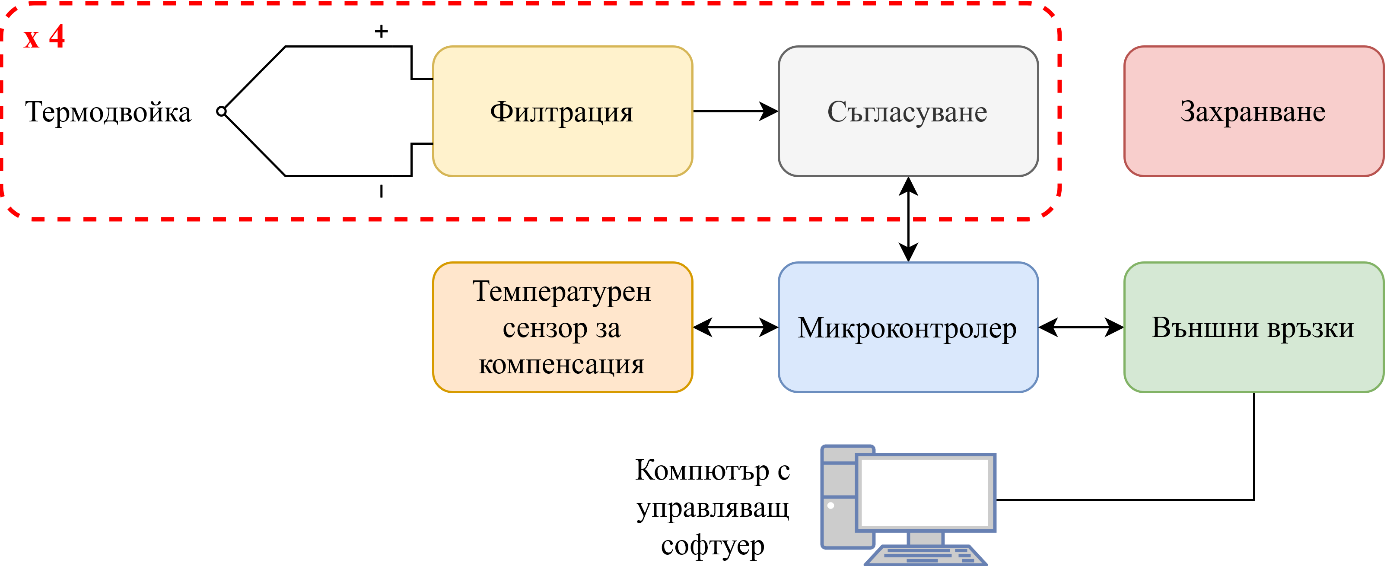
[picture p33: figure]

Фиг. 4.1. Блокова схема на устройството

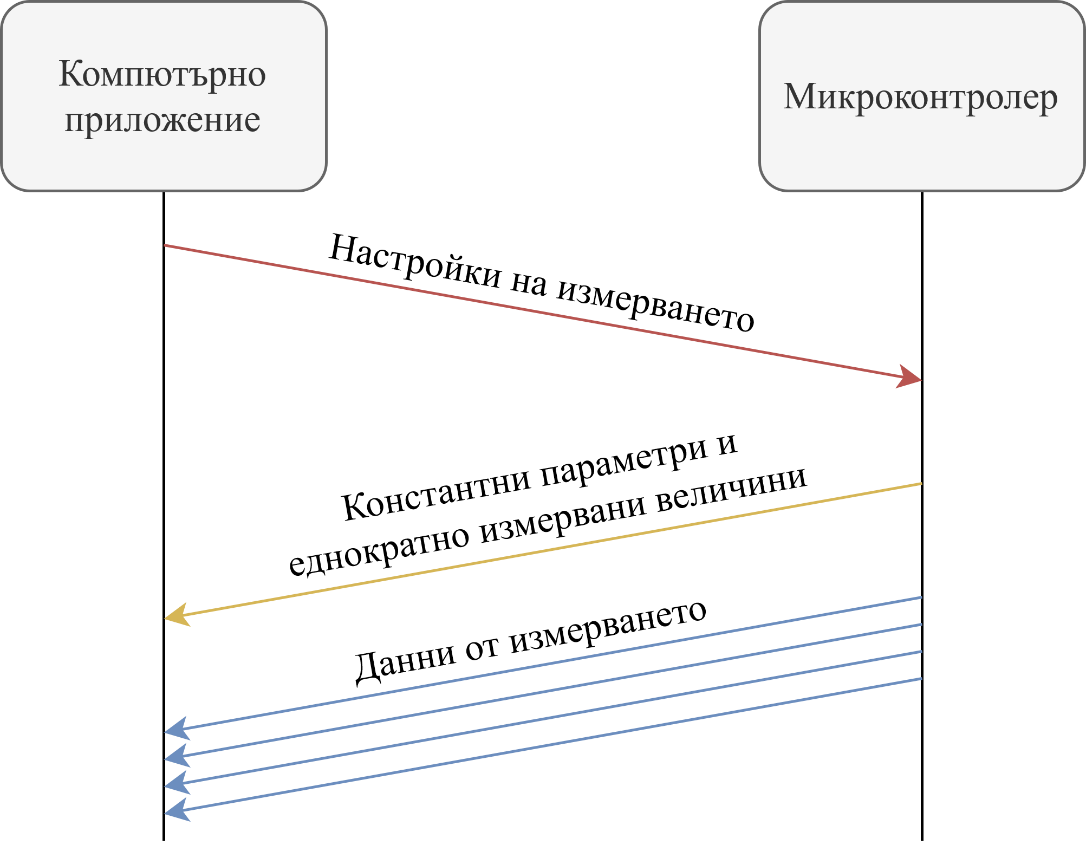
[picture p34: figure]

Фиг. 7.2.1. Комуникационен протокол

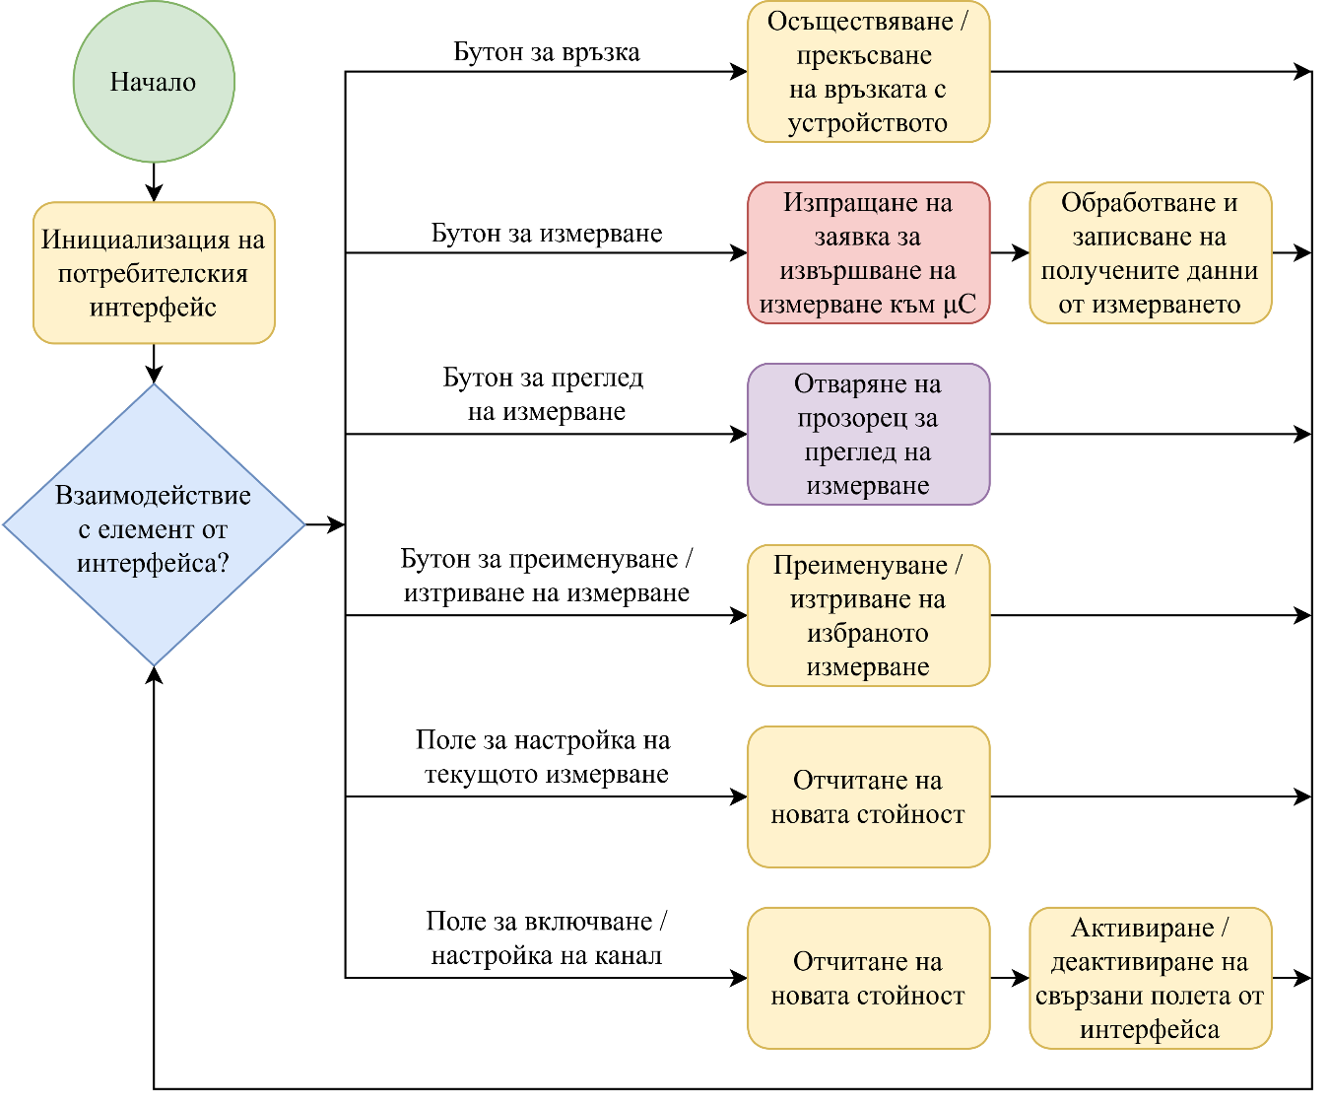
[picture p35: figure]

Фиг. 7.3.2. Алгоритъм на работа на главния прозорец на приложението

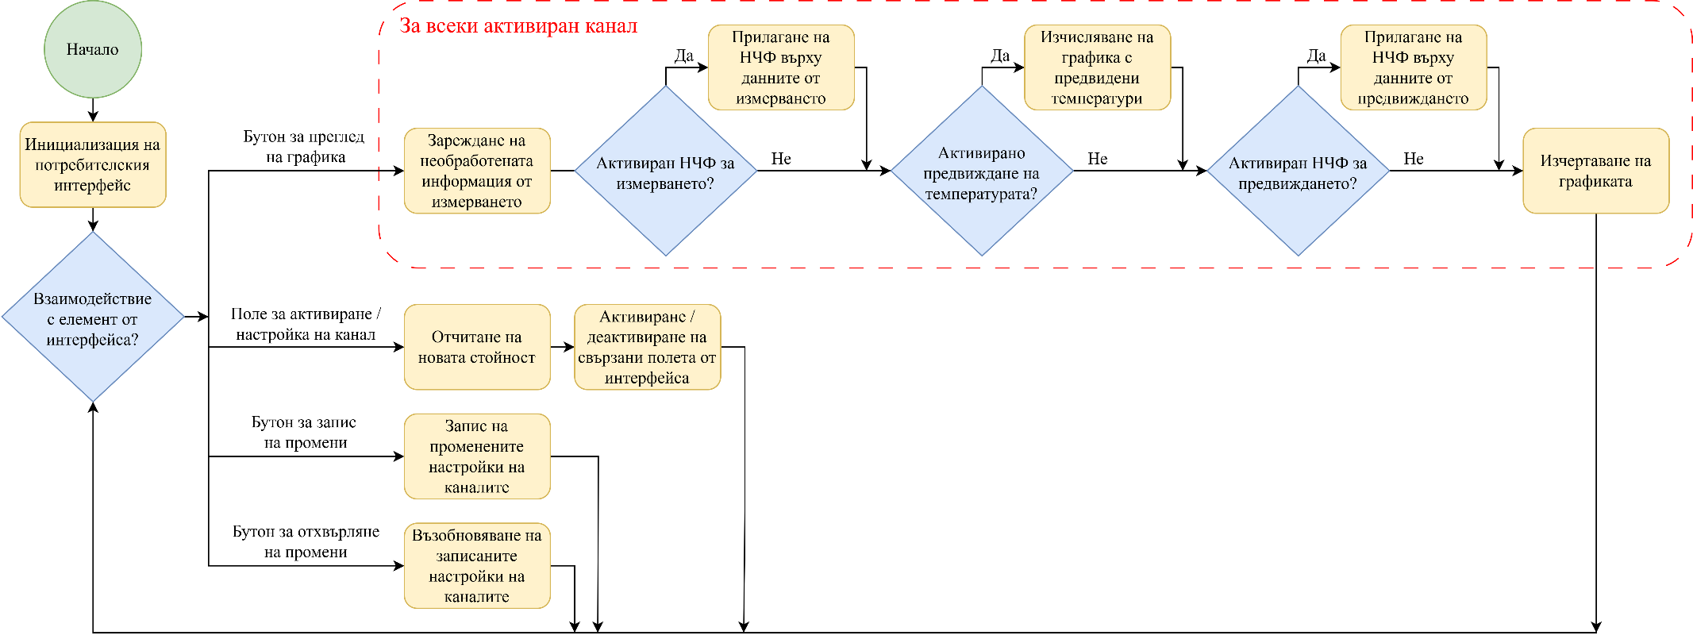
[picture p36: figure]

Фиг. 7.3.5. Алгоритъм на работа на прозорец за преглед на измерване

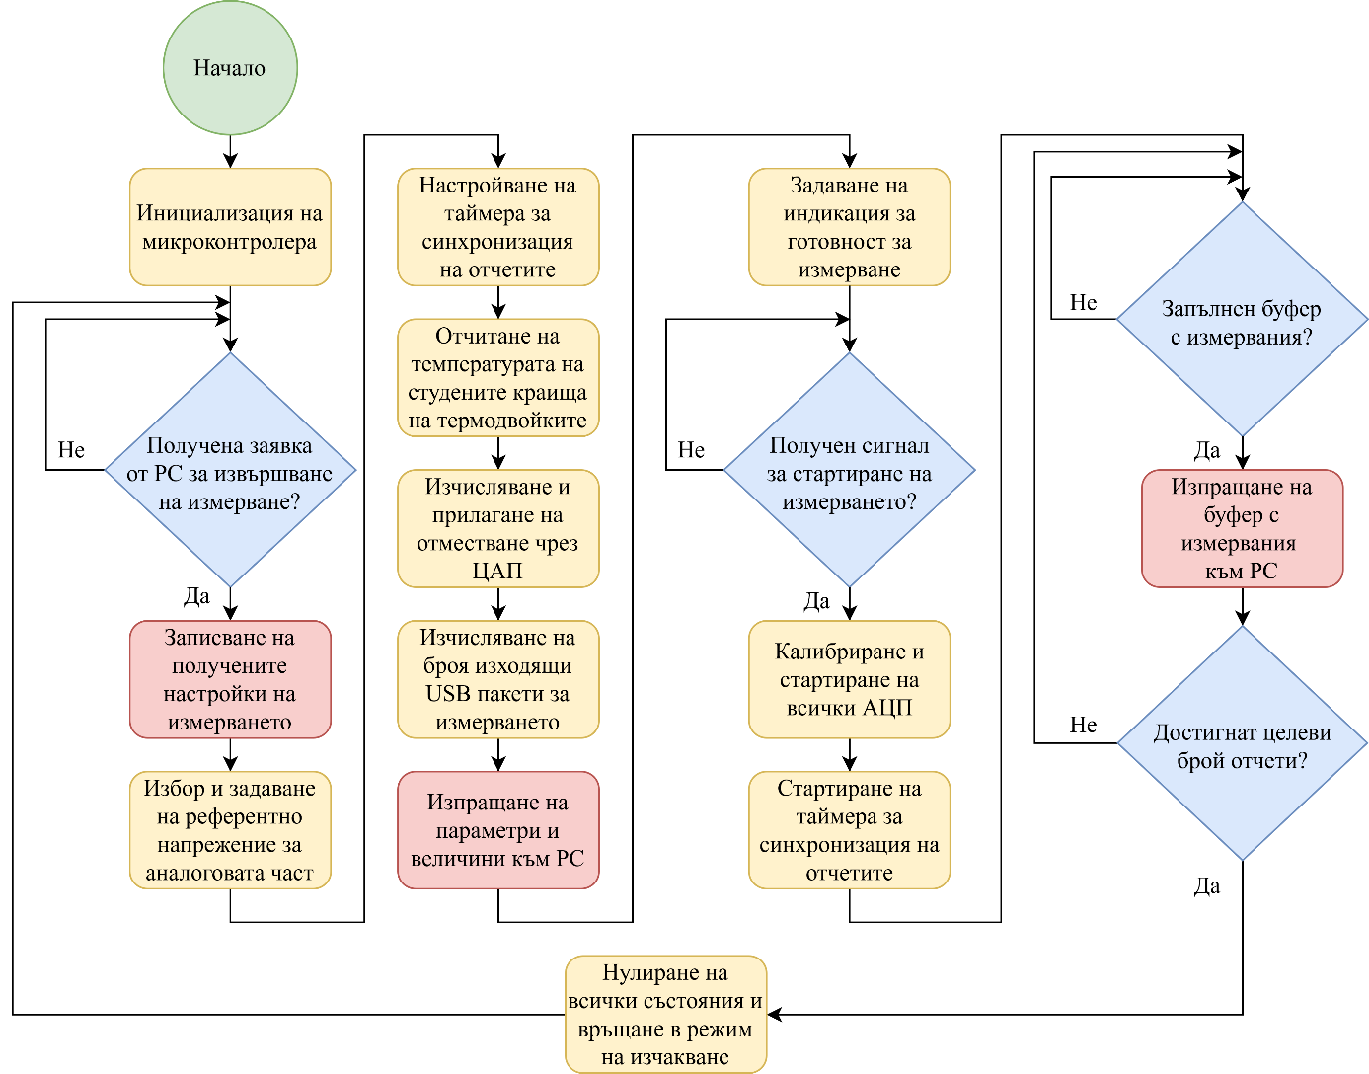
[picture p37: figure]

Фиг. 7.4.1. Алгоритъм на работа на микроконтролера

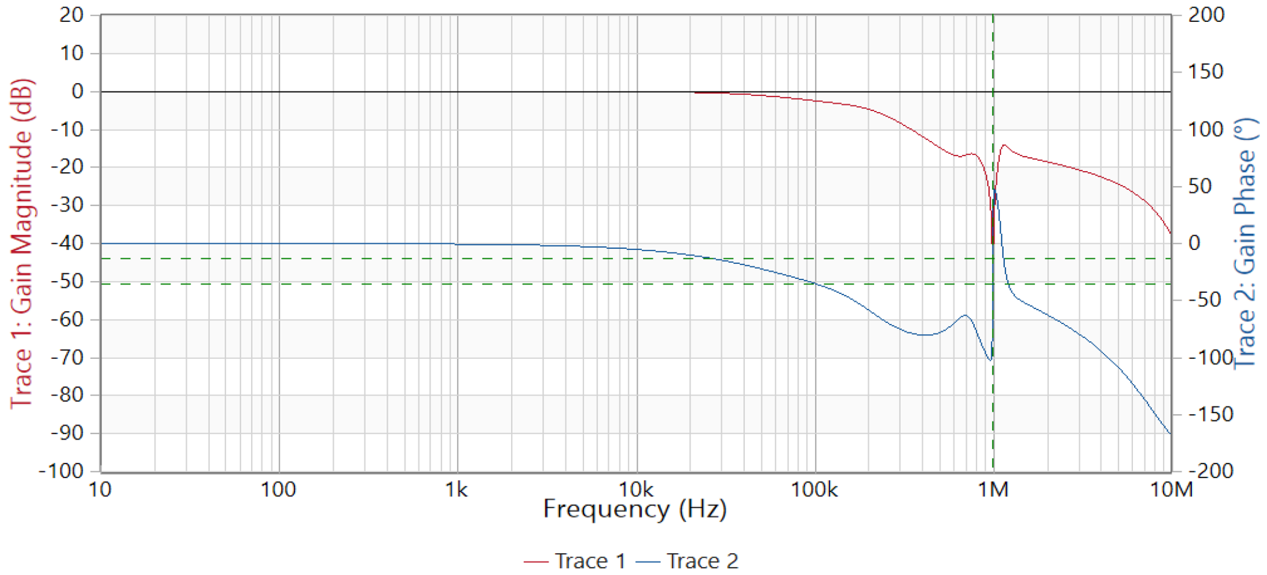
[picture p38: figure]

Фиг. 8.3. АЧХ и ФЧХ на филтрите в обхвата 10 Hz – 10 MHz

Приложение 1

Принципна електрическа схема

Приложение 2

Печатна платка - слоеве

Приложение 3

Печатна платка - монтажен чертеж

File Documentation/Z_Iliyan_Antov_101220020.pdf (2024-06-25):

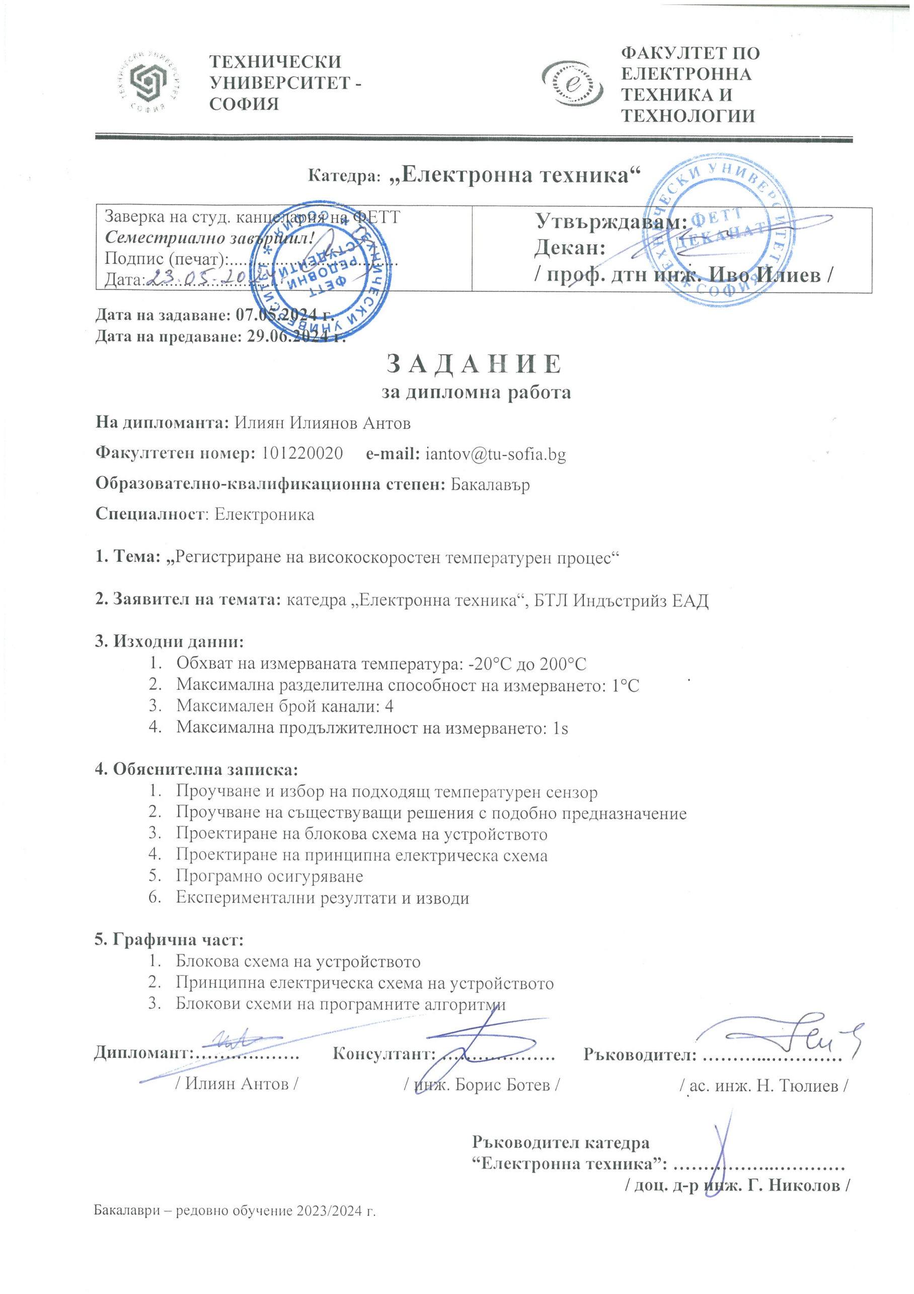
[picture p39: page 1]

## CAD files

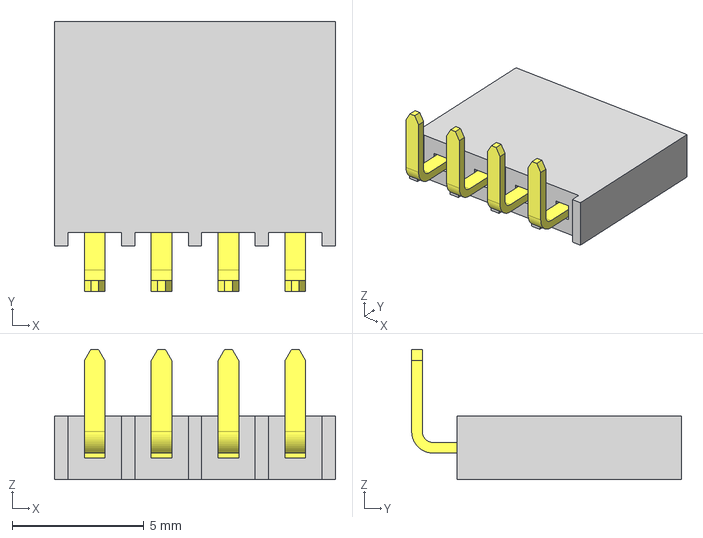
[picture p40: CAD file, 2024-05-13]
Schematics/high-speed-thermocouple-logger/3D models/SSW-104-02-T-S-RA.stp
10.7 x 10.2 x 4.94 mm
T1SSW-104-02-T-S-RA
P2SSW-104-02-T-S-RA

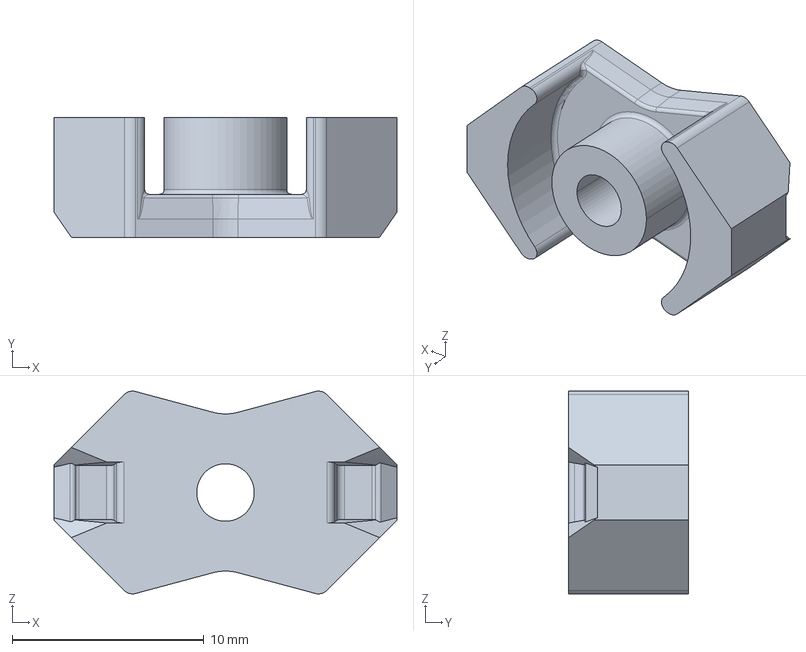
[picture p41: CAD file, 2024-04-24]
Schematics/high-speed-thermocouple-logger/3D models/RM6_M33.step
17.9 x 6.25 x 10.6 mm

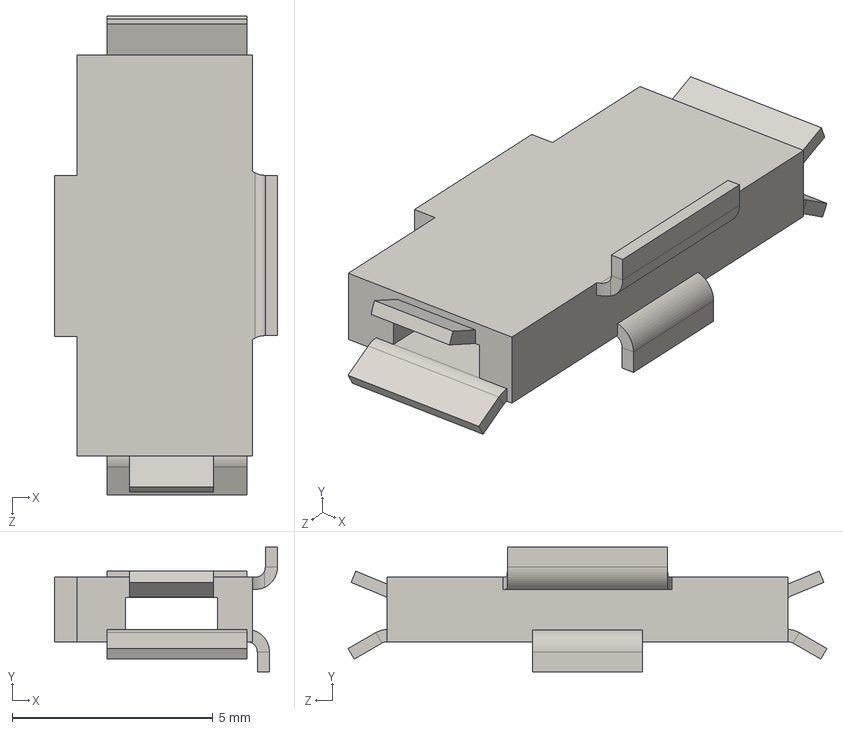
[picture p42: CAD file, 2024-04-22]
Schematics/high-speed-thermocouple-logger/3D models/PCC-SMD-1000.stp
5.56 x 3.11 x 11.9 mm

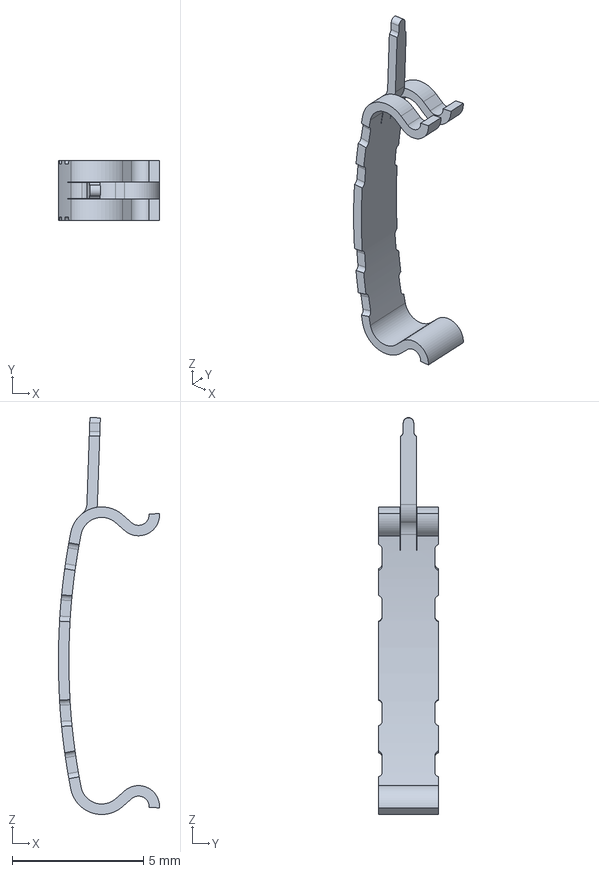
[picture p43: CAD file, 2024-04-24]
Schematics/high-speed-thermocouple-logger/3D models/B65808B2203X000.step
3.84 x 2.30 x 15.1 mm

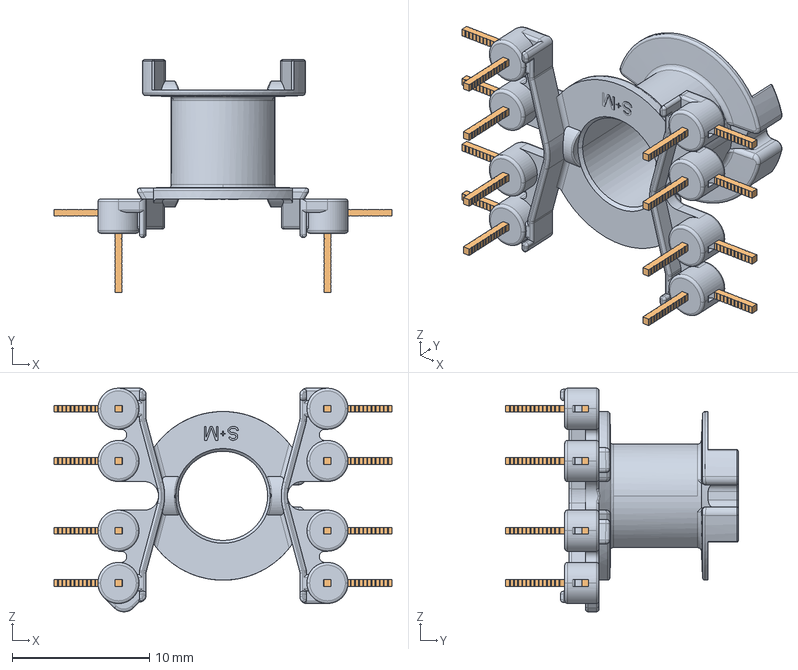
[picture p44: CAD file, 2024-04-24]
Schematics/high-speed-thermocouple-logger/3D models/B65808E1508T001.step
24.6 x 16.9 x 16.3 mm
RM6
DRAT x 8

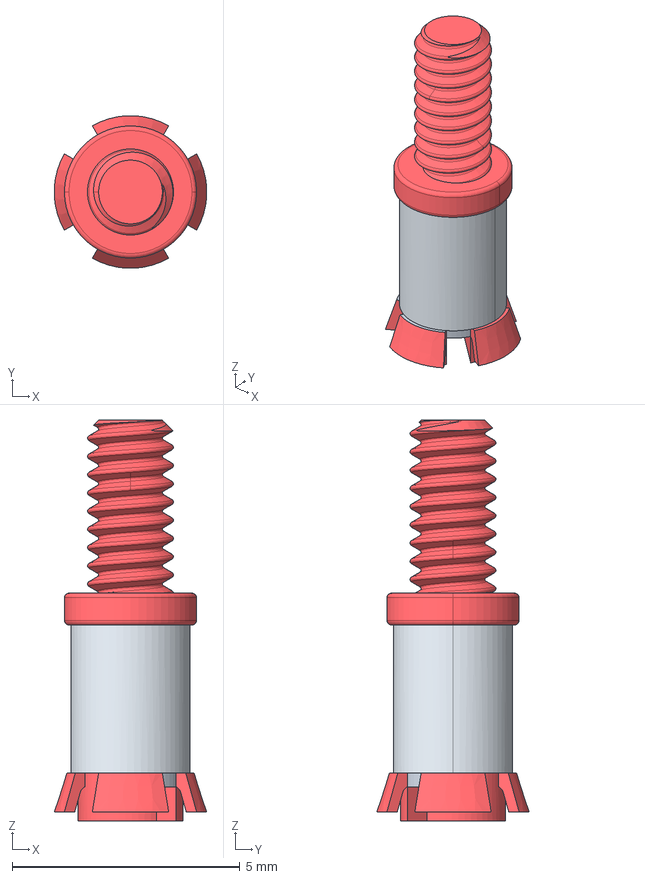
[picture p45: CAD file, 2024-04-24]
Schematics/high-speed-thermocouple-logger/3D models/B65659F0001X023.step
3.34 x 3.34 x 8.80 mm

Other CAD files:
Code/OVERSAMPLE/AN2668_FW_V3.0.0/Project/ADCOversampling-STM32L/TriangularDitherMethod/TASKING/STM32L152-EVAL/Debug/User/main.obj
Code/OVERSAMPLE/AN2668_FW_V3.0.0/Project/ADCOversampling-STM32L/TriangularDitherMethod/TASKING/STM32L152-EVAL/Debug/StdPeriph_Driver/stm32l1xx_tim.obj
Code/OVERSAMPLE/AN2668_FW_V3.0.0/Project/ADCOversampling-STM32L/TriangularDitherMethod/TASKING/STM32L152-EVAL/Debug/StdPeriph_Driver/stm32l1xx_dma.obj
Code/OVERSAMPLE/AN2668_FW_V3.0.0/Project/ADCOversampling-STM32L/TriangularDitherMethod/TASKING/STM32L152-EVAL/Debug/User/oversampling.obj
Code/OVERSAMPLE/AN2668_FW_V3.0.0/Project/ADCOversampling-STM32L/TriangularDitherMethod/TASKING/STM32L152-EVAL/Debug/StdPeriph_Driver/stm32l1xx_adc.obj
Code/OVERSAMPLE/AN2668_FW_V3.0.0/Project/ADCOversampling-STM32L/TriangularDitherMethod/TASKING/STM32L152-EVAL/Debug/User/stm32l1xx_it.obj
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

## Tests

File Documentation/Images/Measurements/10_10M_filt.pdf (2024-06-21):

## Measurement: Gain / Phase

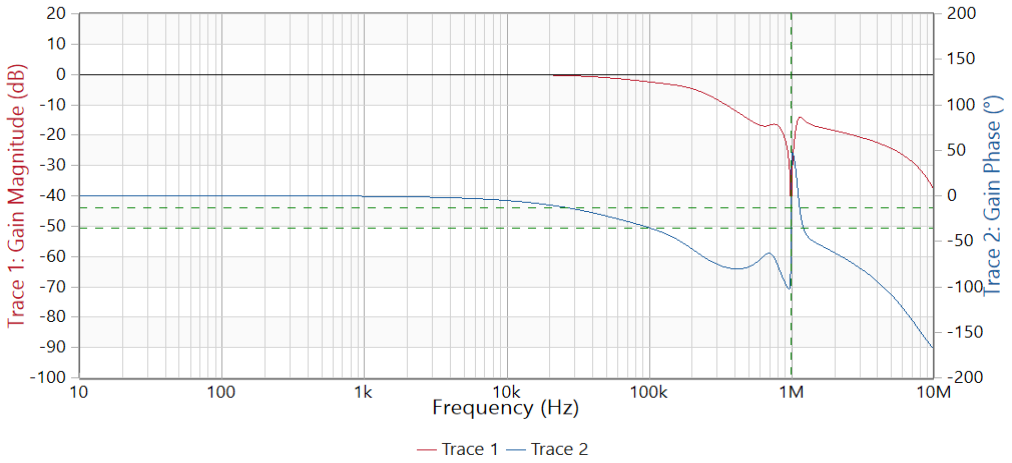
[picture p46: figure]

21-Jun-24, 17:40 | 10_10M_filt.pdf | Page 1/1

Cursor 1
Frequency | 1 MHz
Trace 1 | Magnitude (dB)
Measurement | -43.969 dB
Trace 2 | Phase (°)
Measurement | -35.9 °
Sweep | | Calibration | Full-Range | User-Range
Start frequency: | 10 Hz | Gain | - | -
Stop frequency: | 10 MHz
Center frequency: | 5 MHz | Termination | Channel 1 | Channel 2
Span: | 10 MHz | Gain | 1 MΩ | 1 MΩ
Sweep mode: | Logarithmic
Numer of points: | 1601 | Attenuator setting | Channel 1 | Channel 2
| | Transmission | 20 dB | 20 dB
Hardware setup
Device type: | Bode100R2
Serial number: | QH681K
Receiver bandwidth: | 1 kHz
Output level: | 0 dBm
DUT settling time: | 0 s

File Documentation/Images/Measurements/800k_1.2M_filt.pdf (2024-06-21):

## Measurement: Gain / Phase

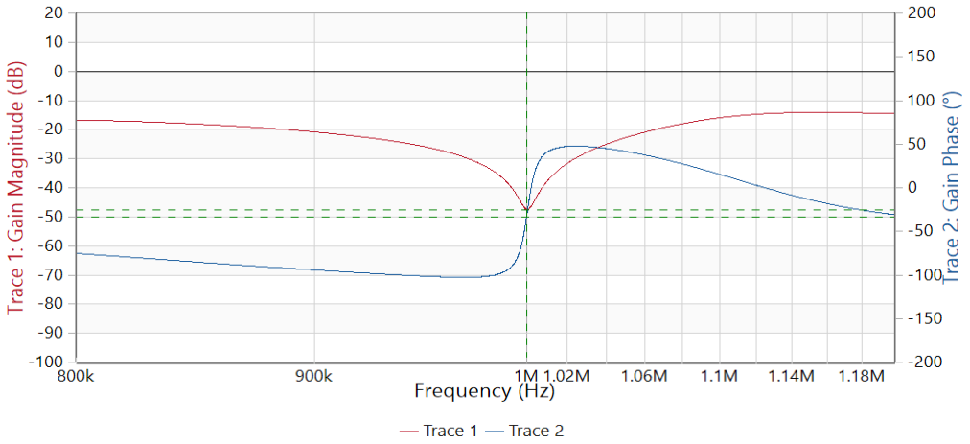
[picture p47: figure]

21-Jun-24, 17:36 | 800k_1.2M_filt.pdf | Page 1/1

Cursor 1
Frequency | 1 MHz
Trace 1 | Magnitude (dB)
Measurement | -47.48 dB
Trace 2 | Phase (°)
Measurement | -33.223 °
Sweep | | Calibration | Full-Range | User-Range
Start frequency: | 800 kHz | Gain | - | -
Stop frequency: | 1.2 MHz
Center frequency: | 1 MHz | Termination | Channel 1 | Channel 2
Span: | 400 kHz | Gain | 1 MΩ | 1 MΩ
Sweep mode: | Logarithmic
Numer of points: | 16501 | Attenuator setting | Channel 1 | Channel 2
| | Transmission | 20 dB | 20 dB
Hardware setup
Device type: | Bode100R2
Serial number: | QH681K
Receiver bandwidth: | 1 kHz
Output level: | 0 dBm
DUT settling time: | 0 s

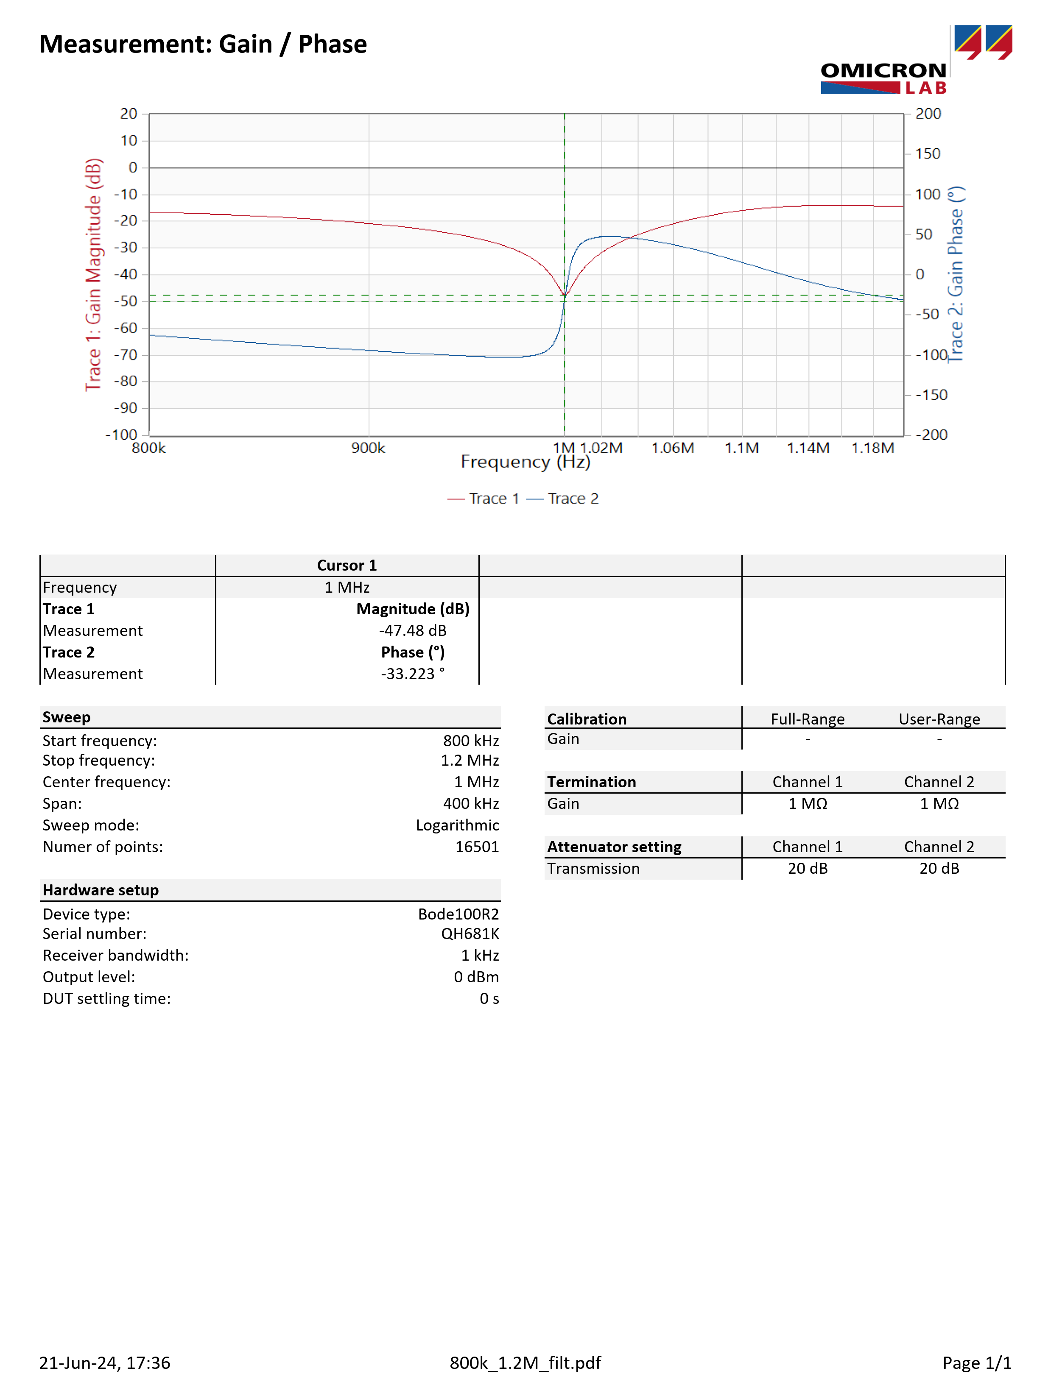
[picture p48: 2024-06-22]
Documentation/Images/Measurements/800k_1.2M_filt_1.png

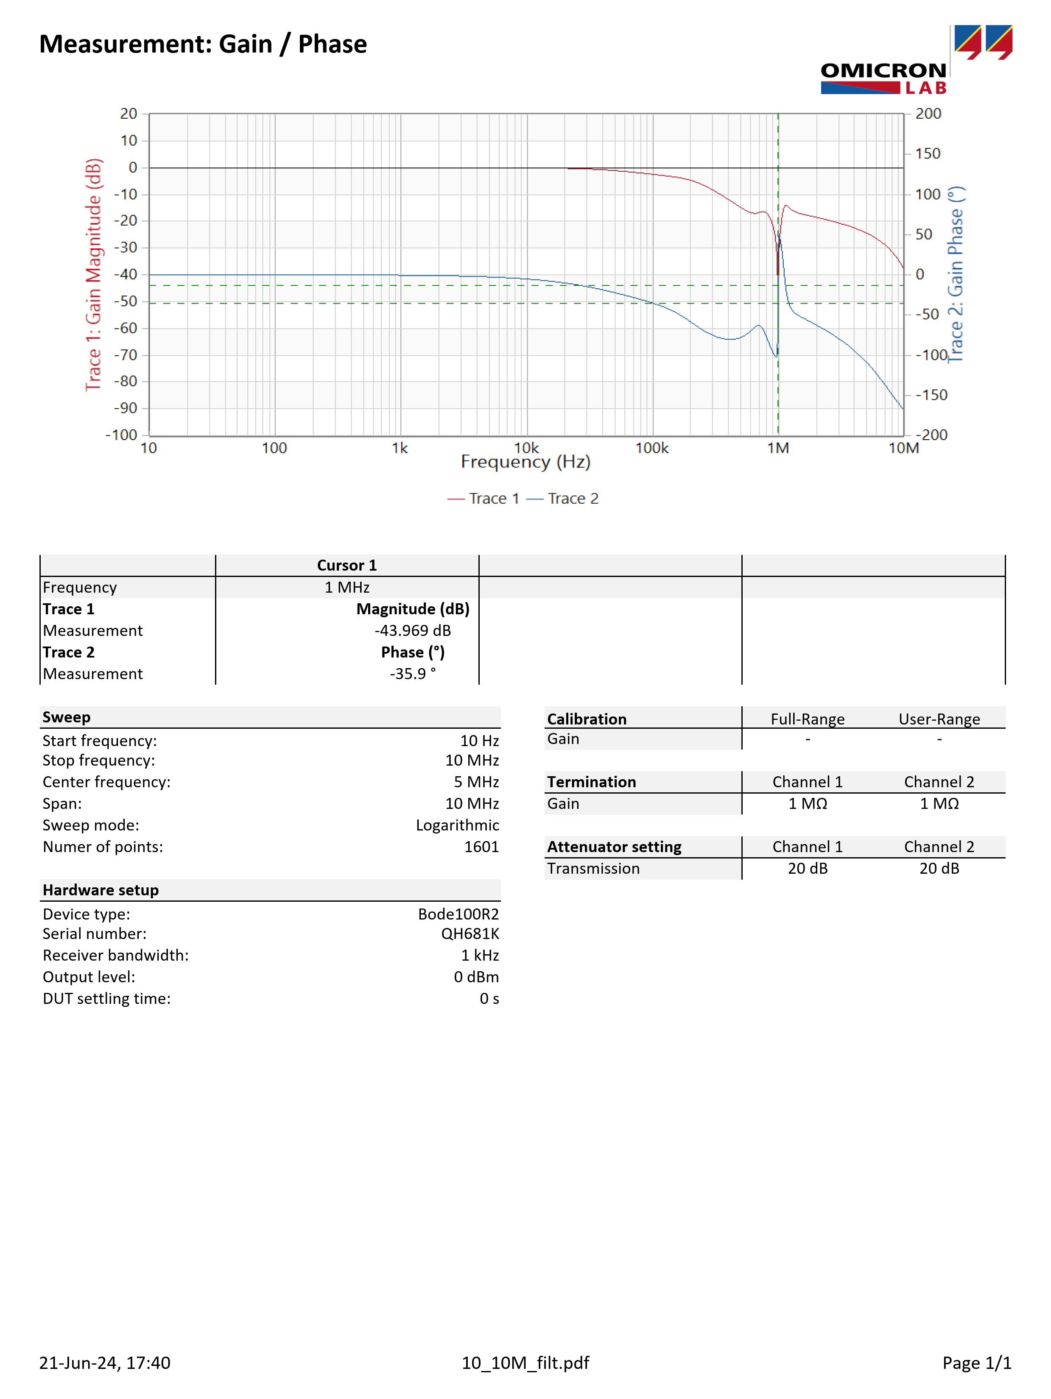
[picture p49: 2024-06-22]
Documentation/Images/Measurements/10_10M_filt_1.png

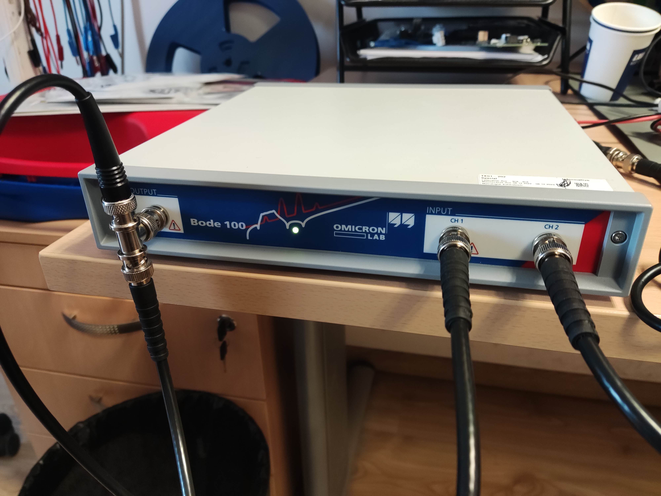
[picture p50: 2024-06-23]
Documentation/Images/Measurements/BodeAnalyzer.jpg

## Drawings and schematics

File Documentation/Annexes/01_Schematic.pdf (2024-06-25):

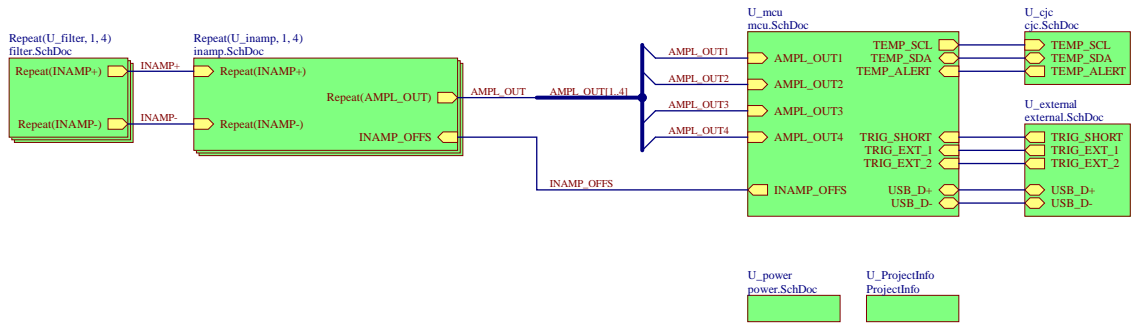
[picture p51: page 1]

Nazev listu/sheet name/: Top.SchDoc | DPS projekt/PCB project/: V286-tclogger

Kreslil /drawn by/ : Iliyan Antov | Kontroloval /checked by/: Boris Botev

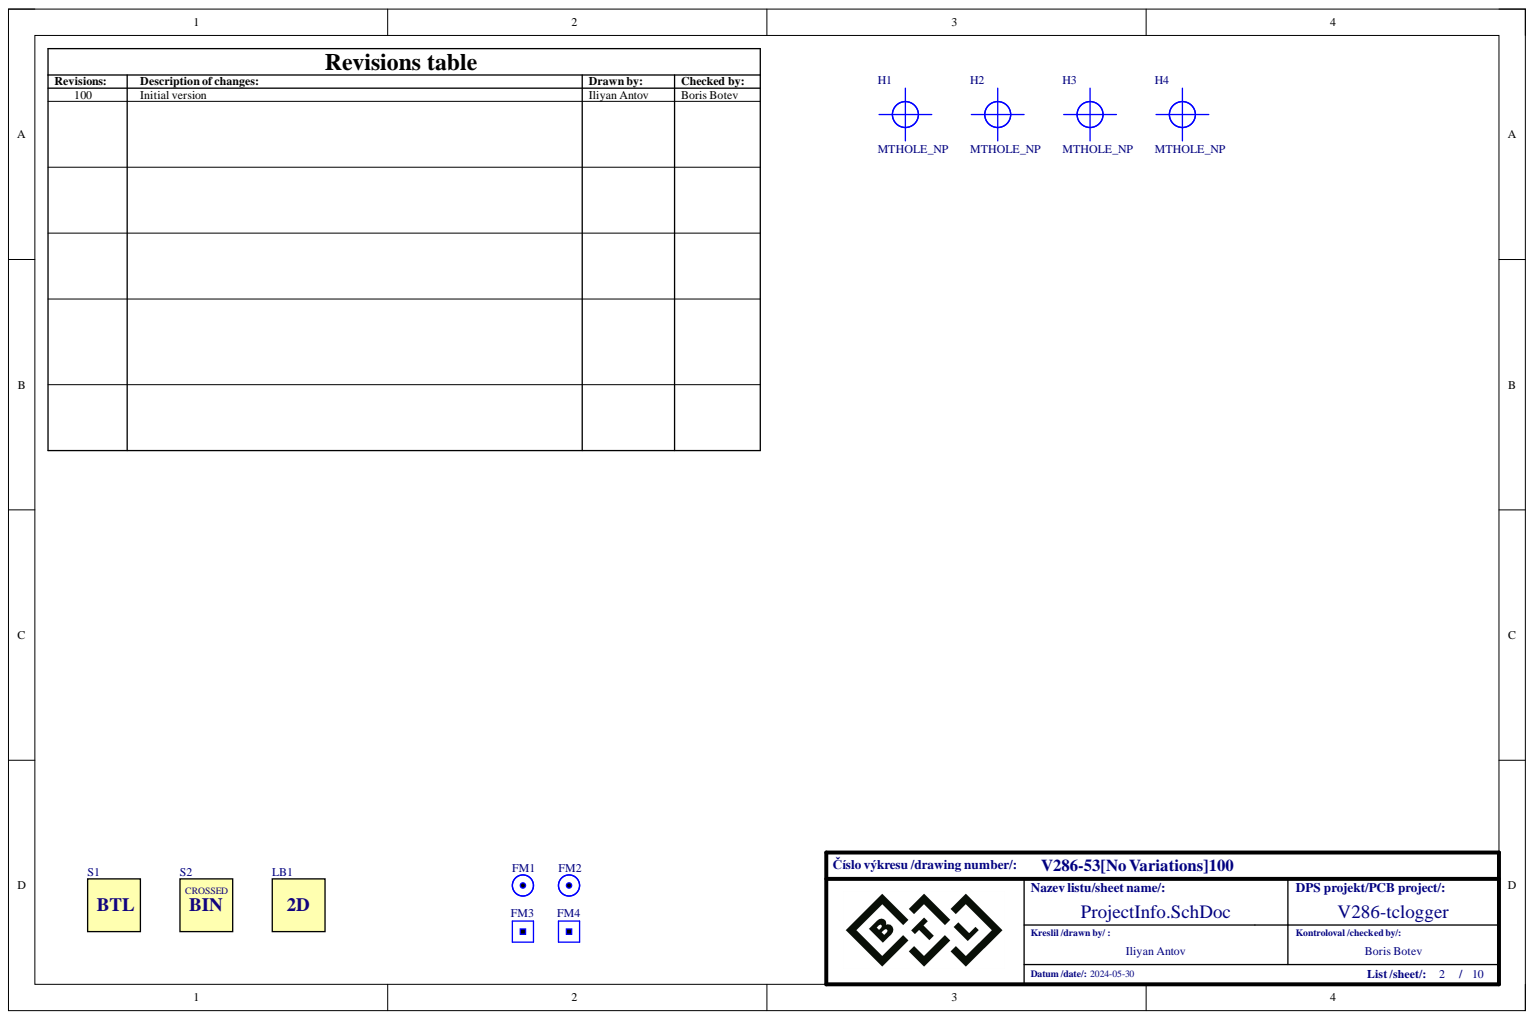
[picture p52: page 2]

Revisions: | Description of changes: | Drawn by: | Checked by:
100 | Initial version | Iliyan Antov | Boris Botev

Nazev listu/sheet name/:
ProjectInfo.SchDoc

DPS projekt/PCB project/:
V286-tclogger

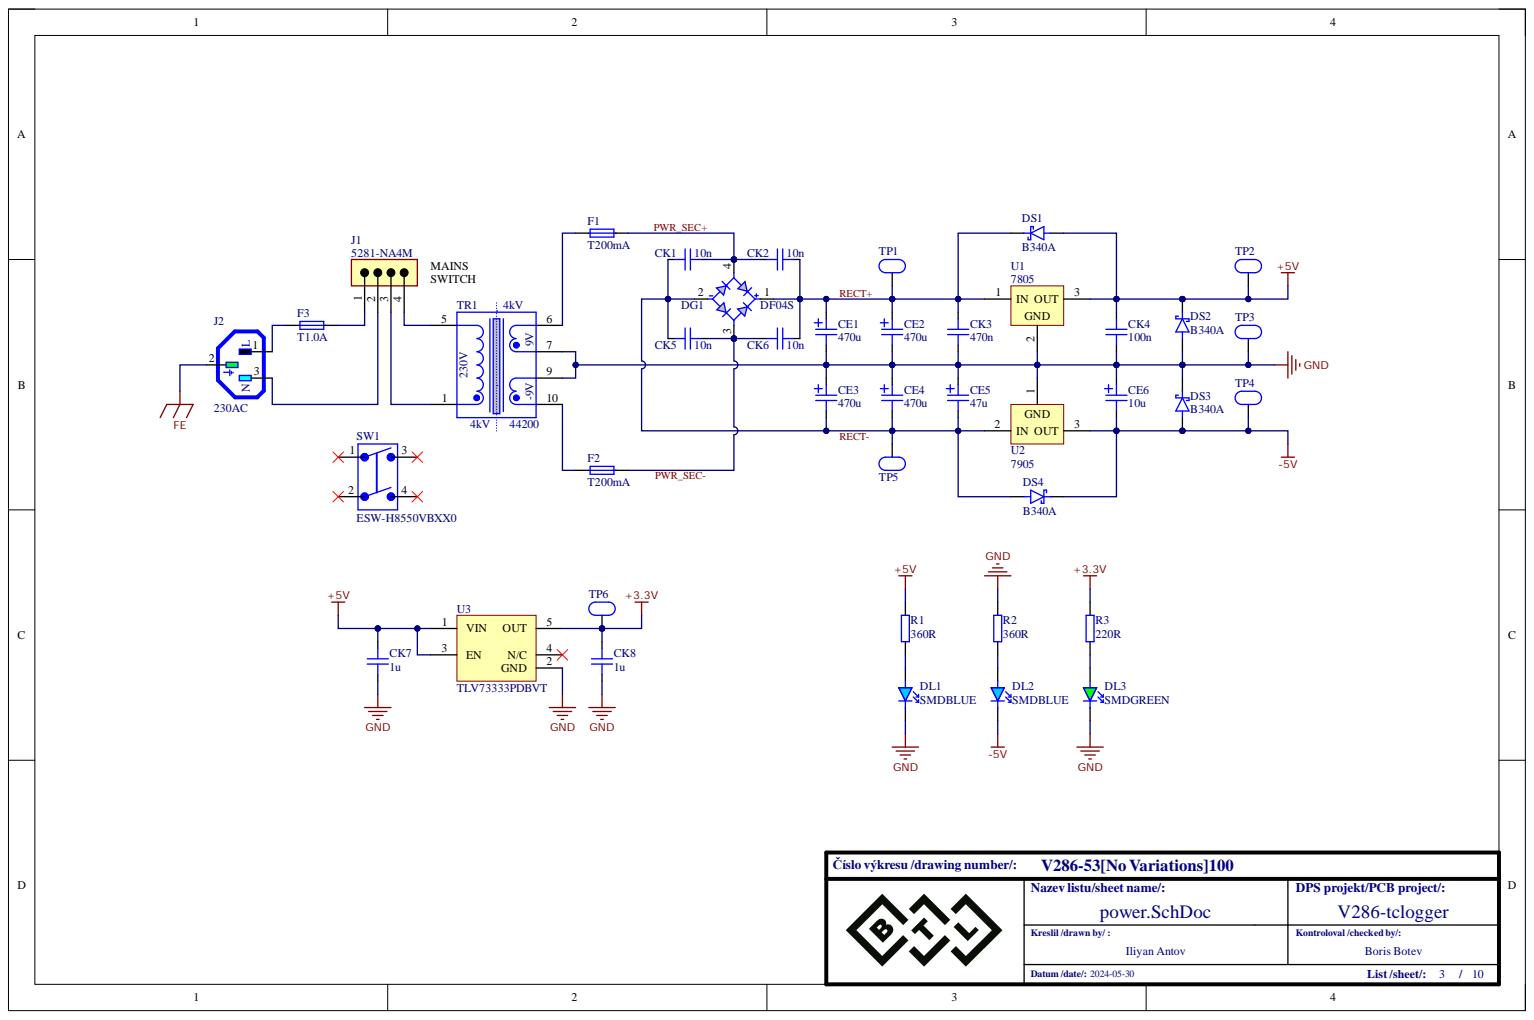
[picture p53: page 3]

Nazev listu/sheet name/: power.SchDoc | DPS projekt/PCB project/: V286-tclogger

Kreslil /drawn by/ : Iliyan Antov | Kontroloval /checked by/: Boris Botev

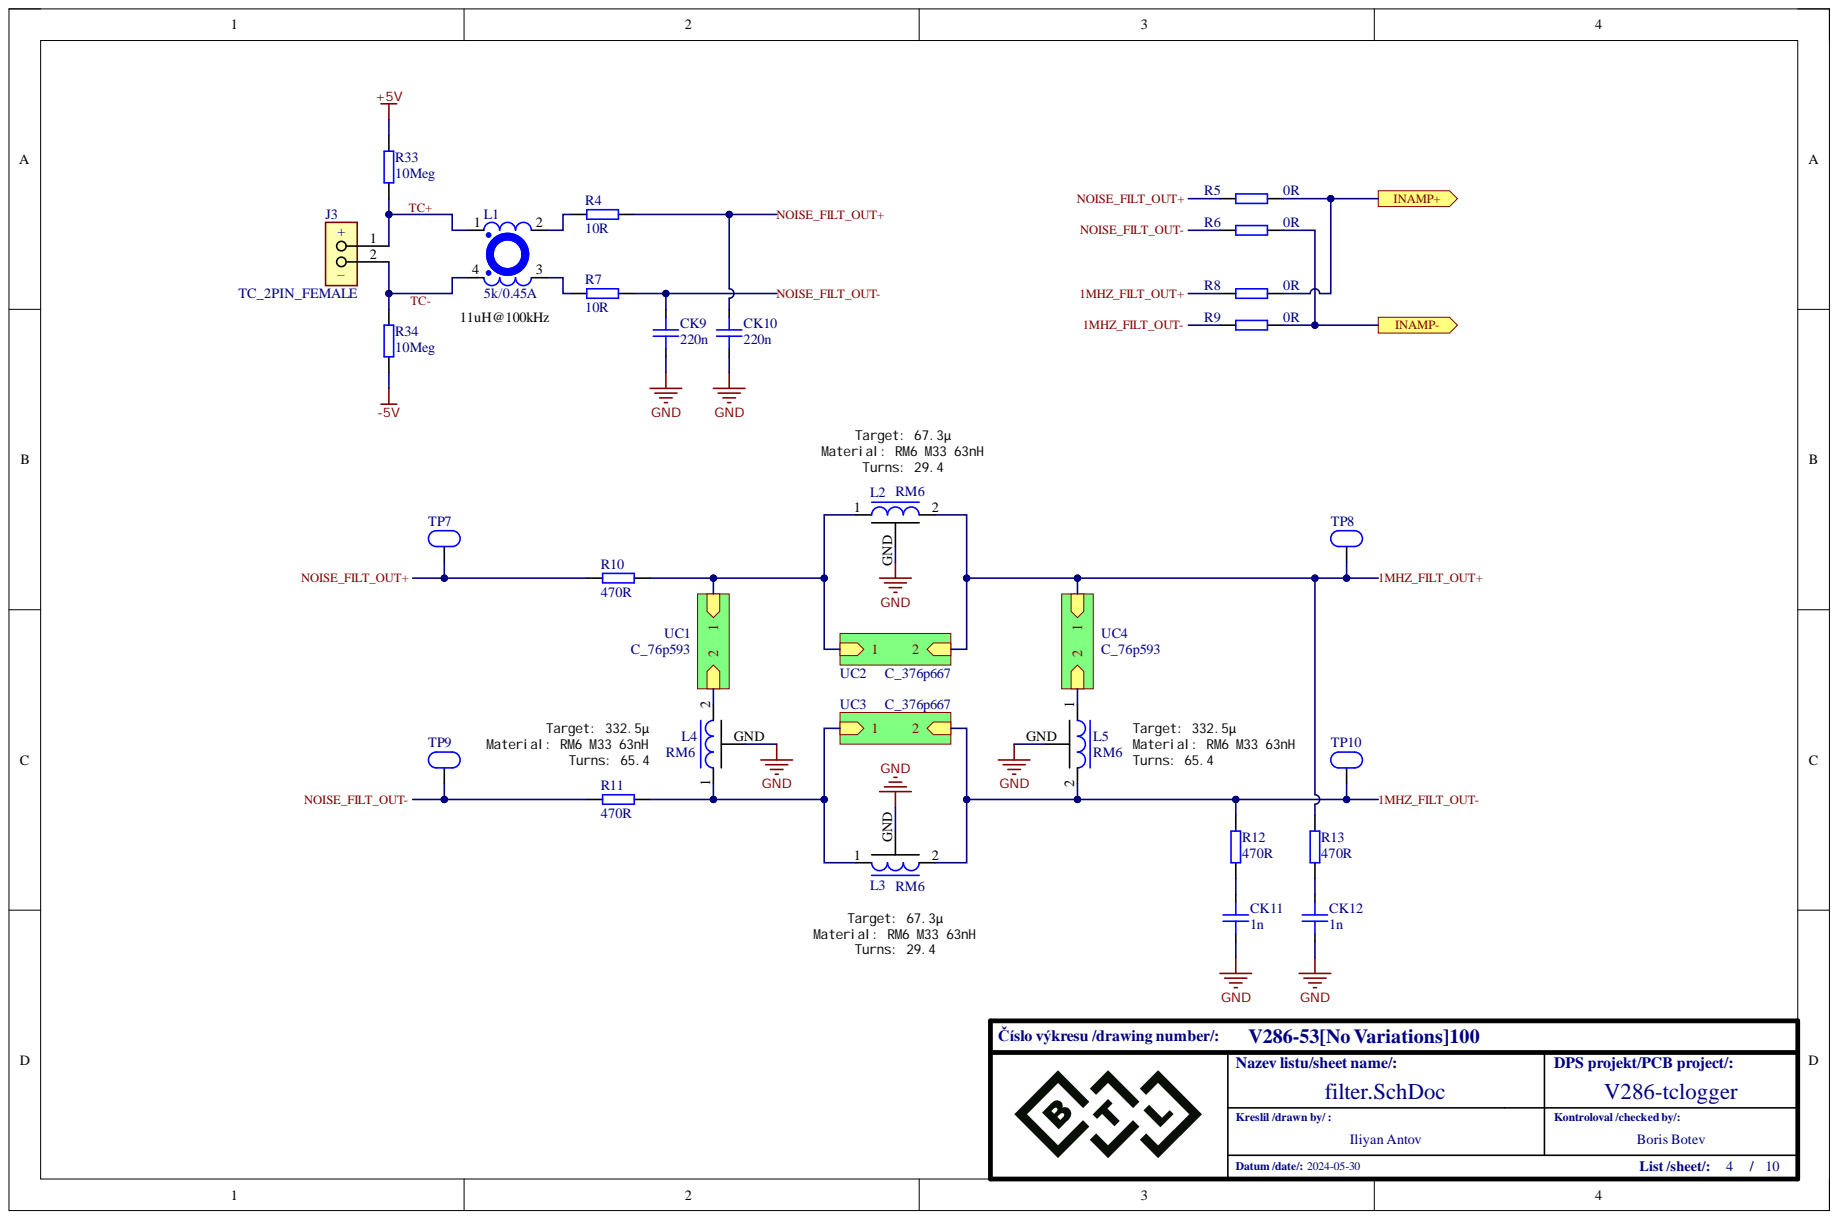
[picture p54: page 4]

Nazev listu/sheet name/: filter.SchDoc | DPS projekt/PCB project/: V286-tclogger

Kreslil /drawn by/ : Iliyan Antov | Kontroloval /checked by/: Boris Botev

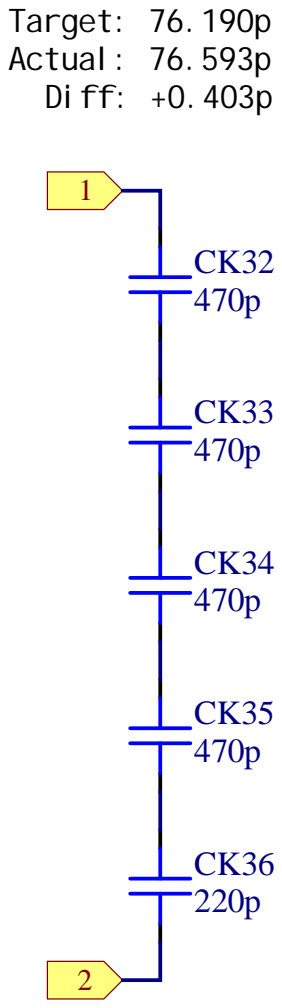
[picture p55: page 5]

Nazev listu/sheet name/: C_76p593.SchDoc | DPS projekt/PCB project/: V286-tclogger

Kreslil /drawn by/ : Iliyan Antov | Kontroloval /checked by/: Boris Botev

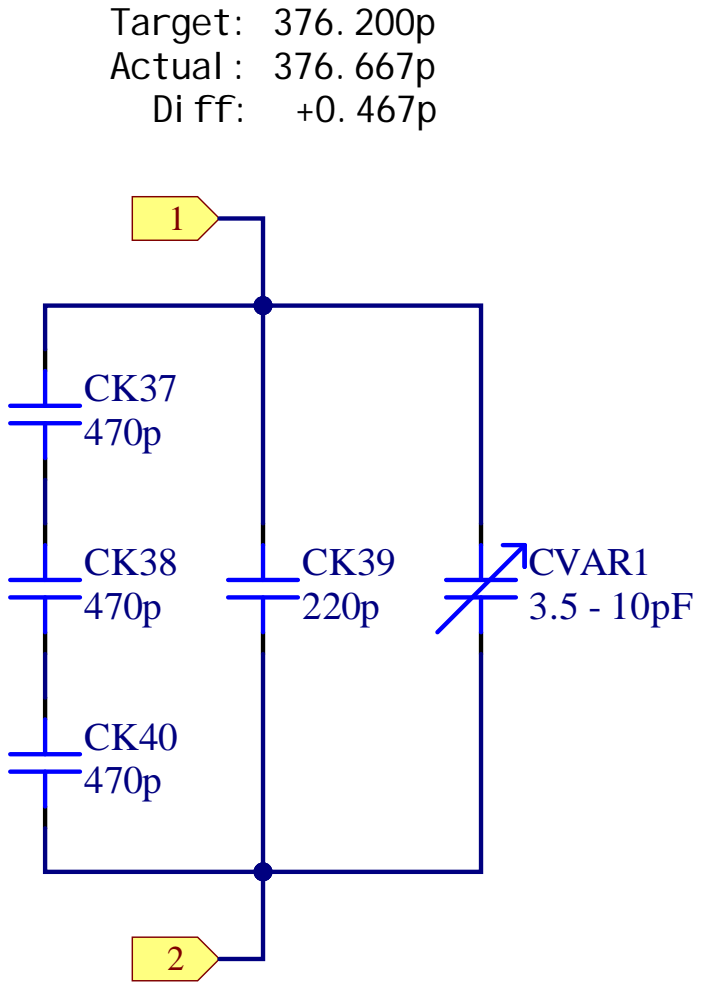
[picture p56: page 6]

Nazev listu/sheet name/: C_376p667.SchDoc | DPS projekt/PCB project/: V286-tclogger

Kreslil /drawn by/ : Iliyan Antov | Kontroloval /checked by/: Boris Botev

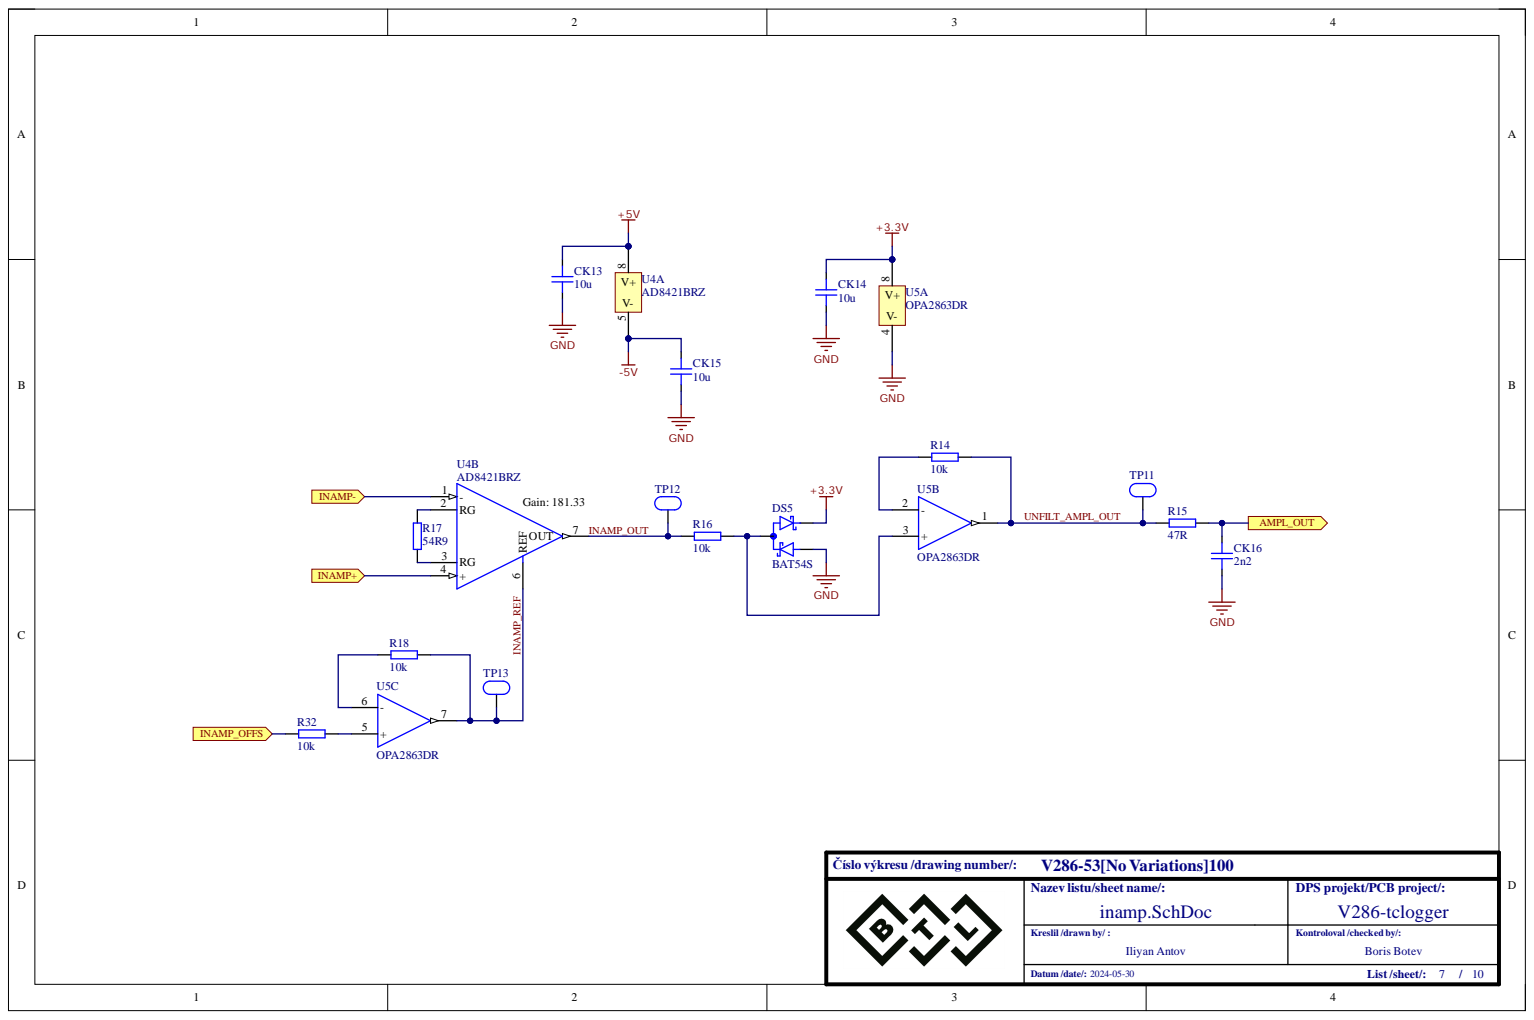
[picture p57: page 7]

Nazev listu/sheet name/: inamp.SchDoc | DPS projekt/PCB project/: V286-tclogger

Kreslil /drawn by/ : Iliyan Antov | Kontroloval /checked by/: Boris Botev

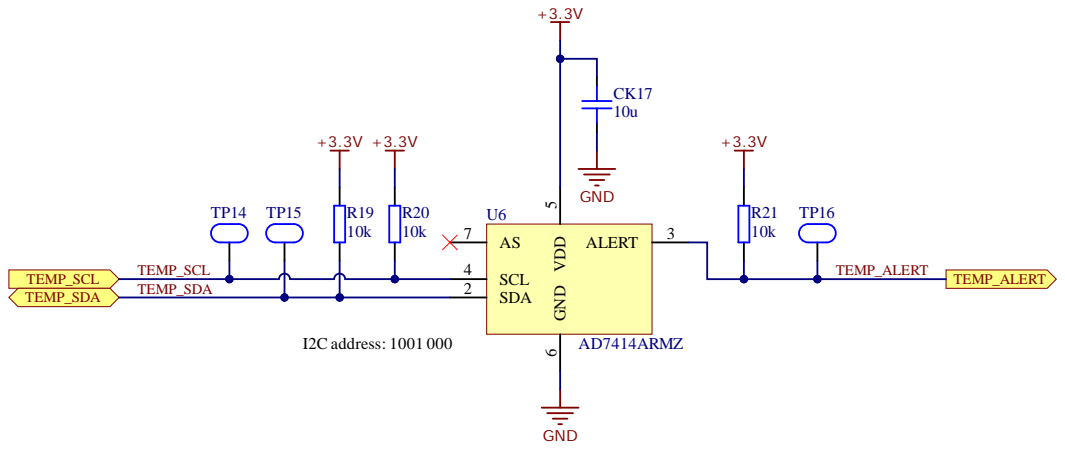
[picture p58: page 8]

Nazev listu/sheet name/: cjc.SchDoc | DPS projekt/PCB project/: V286-tclogger

Kreslil /drawn by/ : Iliyan Antov | Kontroloval /checked by/: Boris Botev

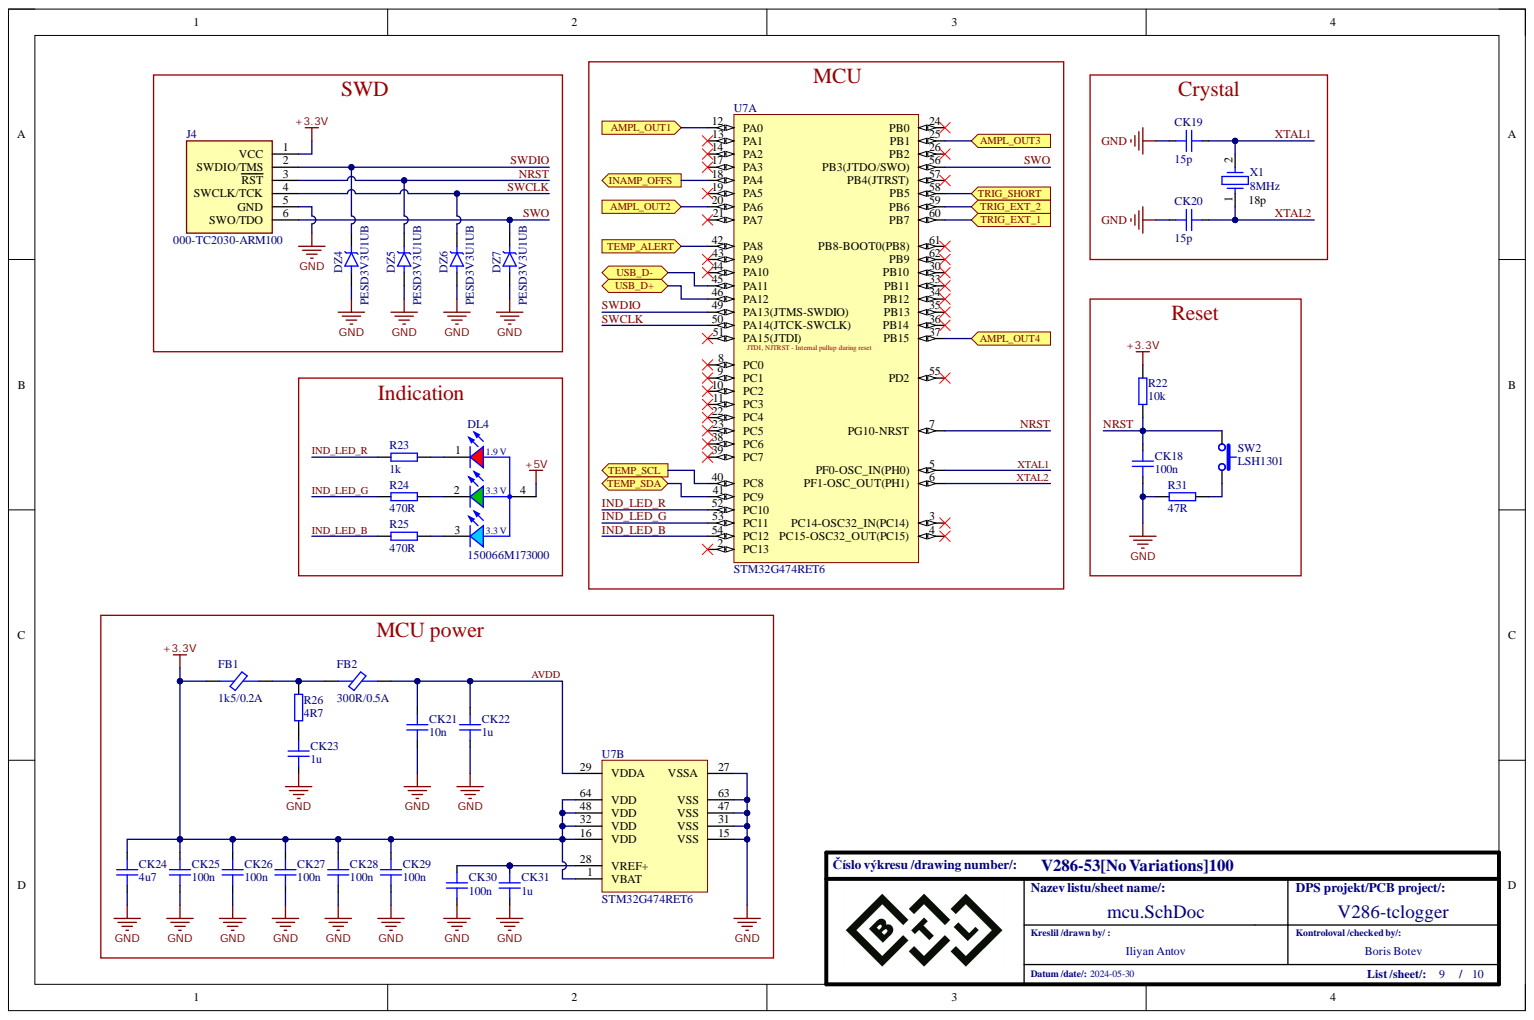
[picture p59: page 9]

Nazev listu/sheet name/:

DPS projekt/PCB project/:
V286-tclogger

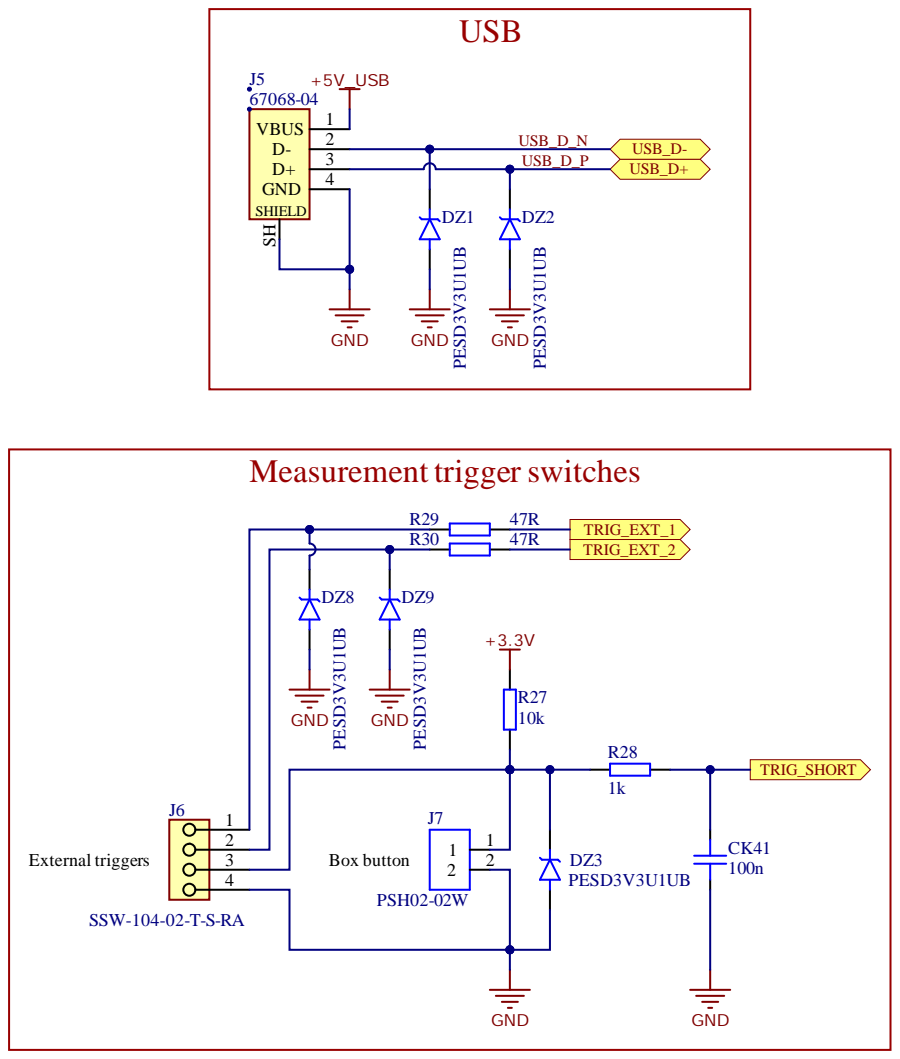
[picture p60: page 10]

Nazev listu/sheet name/: external.SchDoc | DPS projekt/PCB project/: V286-tclogger

Kreslil /drawn by/ : Iliyan Antov | Kontroloval /checked by/: Boris Botev

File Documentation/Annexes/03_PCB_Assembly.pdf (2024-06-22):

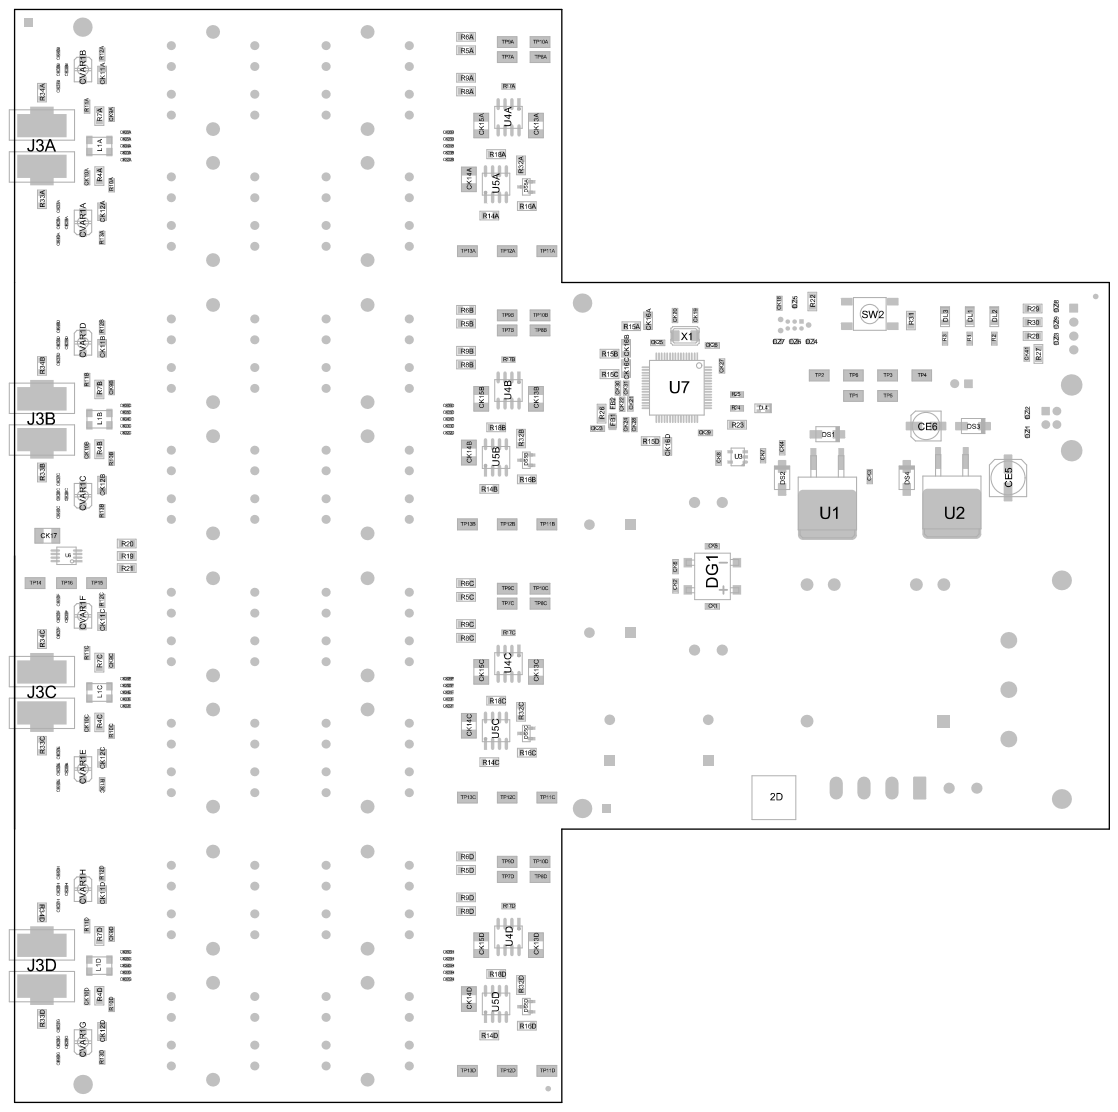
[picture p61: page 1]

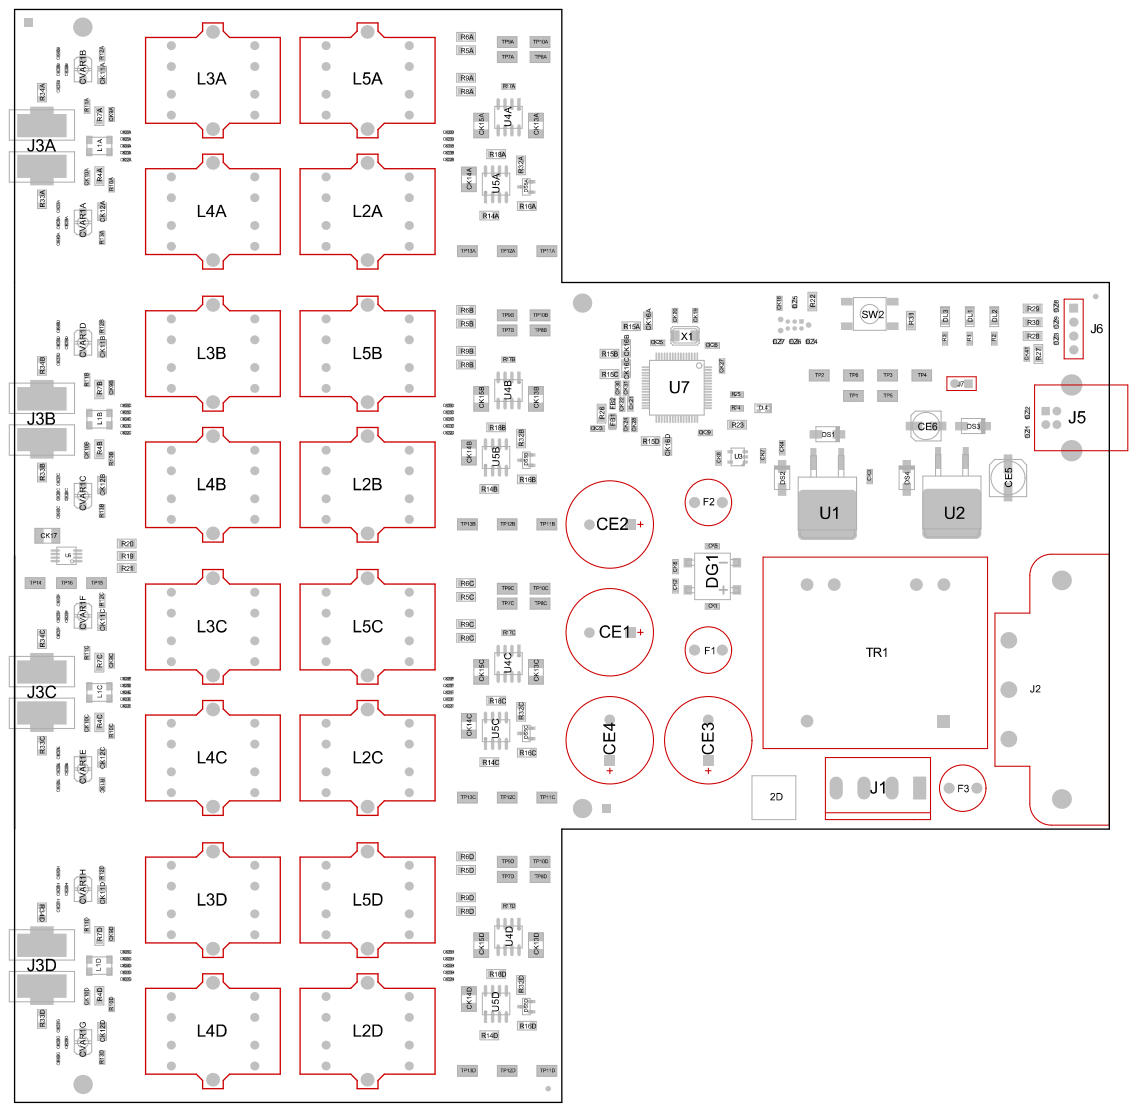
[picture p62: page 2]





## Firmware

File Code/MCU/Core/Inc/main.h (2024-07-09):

/* USER CODE BEGIN Header */
/**
  ******************************************************************************
  * @file           : main.h
  * @brief          : Header for main.c file.
  *                   This file contains the common defines of the application.
  ******************************************************************************
  * @attention
  *
  * Copyright (c) 2024 STMicroelectronics.
  * All rights reserved.
  *
  * This software is licensed under terms that can be found in the LICENSE file
  * in the root directory of this software component.
  * If no LICENSE file comes with this software, it is provided AS-IS.
  *
  ******************************************************************************
  */
/* USER CODE END Header */

/* Define to prevent recursive inclusion -------------------------------------*/
#ifndef __MAIN_H
#define __MAIN_H

#ifdef __cplusplus
extern "C" {
#endif

/* Includes ------------------------------------------------------------------*/
#include "stm32g4xx_hal.h"

/* Private includes ----------------------------------------------------------*/
/* USER CODE BEGIN Includes */
#include <math.h>
/* USER CODE END Includes */

/* Exported types ------------------------------------------------------------*/
/* USER CODE BEGIN ET */
enum PROG_STATE {
  IDLE,
  CFG_RECEIVED,
  CFG_INTERPRETED,
  PARAMETERS_SET,
  ARMED,
  MEASURING,
  REPORTING,
  DONE
};

enum ADC_BUFFER_STATE {
	EMPTY,
	START_FULL,
	END_FULL
};

/* USER CODE END ET */

/* Exported constants --------------------------------------------------------*/
/* USER CODE BEGIN EC */

/* USER CODE END EC */

/* Exported macro ------------------------------------------------------------*/
/* USER CODE BEGIN EM */

/* USER CODE END EM */

/* Exported functions prototypes ---------------------------------------------*/
void Error_Handler(void);

/* USER CODE BEGIN EFP */

/* USER CODE END EFP */

/* Private defines -----------------------------------------------------------*/
#define ERRATA_FIX1_Pin GPIO_PIN_10
#define ERRATA_FIX1_GPIO_Port GPIOB
#define ERRATA_FIX2_Pin GPIO_PIN_11
#define ERRATA_FIX2_GPIO_Port GPIOB
#define ERRATA_FIX3_Pin GPIO_PIN_13
#define ERRATA_FIX3_GPIO_Port GPIOB
#define ERRATA_FIX4_Pin GPIO_PIN_14
#define ERRATA_FIX4_GPIO_Port GPIOB
#define TEMP_SCL_Pin GPIO_PIN_8
#define TEMP_SCL_GPIO_Port GPIOC
#define TEMP_SDA_Pin GPIO_PIN_9
#define TEMP_SDA_GPIO_Port GPIOC
#define TEMP_ALERT_Pin GPIO_PIN_8
#define TEMP_ALERT_GPIO_Port GPIOA
#define T_SWDIO_Pin GPIO_PIN_13
#define T_SWDIO_GPIO_Port GPIOA
#define T_SWCLK_Pin GPIO_PIN_14
#define T_SWCLK_GPIO_Port GPIOA
#define IND_LED_R_Pin GPIO_PIN_10
#define IND_LED_R_GPIO_Port GPIOC
#define IND_LED_G_Pin GPIO_PIN_11
#define IND_LED_G_GPIO_Port GPIOC
#define IND_LED_B_Pin GPIO_PIN_12
#define IND_LED_B_GPIO_Port GPIOC
#define T_SWO_Pin GPIO_PIN_3
#define T_SWO_GPIO_Port GPIOB
#define TRIG_SHORT_Pin GPIO_PIN_5
#define TRIG_SHORT_GPIO_Port GPIOB
#define TRIG_SHORT_EXTI_IRQn EXTI9_5_IRQn
#define TRIG_EXT_2_Pin GPIO_PIN_6
#define TRIG_EXT_2_GPIO_Port GPIOB
#define TRIG_EXT_2_EXTI_IRQn EXTI9_5_IRQn
#define TRIG_EXT_1_Pin GPIO_PIN_7
#define TRIG_EXT_1_GPIO_Port GPIOB
#define TRIG_EXT_1_EXTI_IRQn EXTI9_5_IRQn

/* USER CODE BEGIN Private defines */
#define TEMP_SENSOR_ADDR 0b1001000

#define INAMP_OUTPUT_BUFFER_OFFSET 0.2		// Compensating for the opamp minimum output voltage
#define MINIMUM_TEMPERATURE -20				// °C
#define INAMP_GAIN ((9900 / 54.9) + 1)

#define MAX_CHANNEL_COUNT 4
#define PARAMETERS_MSG_SIZE 256
#define REPORT_MSG_SIZE 256
#define ADC_BUFFER_SIZE 1000									// uint16
#define USB_BUFFER_SIZE ADC_BUFFER_SIZE * MAX_CHANNEL_COUNT		// uint8
#define USB_RX_BUFFER_SIZE 256
#define CFG_VAR_SIZE 64
/* USER CODE END Private defines */

#ifdef __cplusplus
}
#endif

#endif /* __MAIN_H */

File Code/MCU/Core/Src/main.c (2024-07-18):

/* USER CODE BEGIN Header */
/**
  ******************************************************************************
  * @file           : main.c
  * @brief          : Main program body
  ******************************************************************************
  * @attention
  *
  * Copyright (c) 2024 STMicroelectronics.
  * All rights reserved.
  *
  * This software is licensed under terms that can be found in the LICENSE file
  * in the root directory of this software component.
  * If no LICENSE file comes with this software, it is provided AS-IS.
  *
  ******************************************************************************
  */
/* USER CODE END Header */
/* Includes ------------------------------------------------------------------*/
#include "main.h"
#include "usb_device.h"

/* Private includes ----------------------------------------------------------*/
/* USER CODE BEGIN Includes */
#include "usbd_cdc_if.h"
#include "stm32g4xx_ll_usb.h"
#include <string.h>
#include <stdio.h>
/* USER CODE END Includes */

/* Private typedef -----------------------------------------------------------*/
/* USER CODE BEGIN PTD */

/* USER CODE END PTD */

/* Private define ------------------------------------------------------------*/
/* USER CODE BEGIN PD */

/* USER CODE END PD */

/* Private macro -------------------------------------------------------------*/
/* USER CODE BEGIN PM */
extern USBD_HandleTypeDef hUsbDeviceFS;
/* USER CODE END PM */

/* Private variables ---------------------------------------------------------*/
ADC_HandleTypeDef hadc1;
ADC_HandleTypeDef hadc2;
ADC_HandleTypeDef hadc3;
ADC_HandleTypeDef hadc4;
DMA_HandleTypeDef hdma_adc1;
DMA_HandleTypeDef hdma_adc2;
DMA_HandleTypeDef hdma_adc3;
DMA_HandleTypeDef hdma_adc4;

DAC_HandleTypeDef hdac1;

I2C_HandleTypeDef hi2c3;

TIM_HandleTypeDef htim2;

/* USER CODE BEGIN PV */
int current_packet_count = 0;
int target_packet_count = 0;
int dropped_packet_count = 0;

uint16_t adc_buffers[MAX_CHANNEL_COUNT][ADC_BUFFER_SIZE];
int8_t rx_buffer[USB_RX_BUFFER_SIZE];

volatile enum PROG_STATE prog_state = IDLE;
volatile float cold_junction_temp = 0;			// [°C]
volatile float analog_reference_voltage = 2.9;	// [V]
volatile float applied_voltage_offset = 0;		// [V]

uint16_t record_length_ms = 100;
uint16_t record_interval_us = 10;
char tc_type = 'J';
enum ADC_BUFFER_STATE usb_transmition_state = EMPTY;
enum ADC_BUFFER_STATE adc_states[MAX_CHANNEL_COUNT] = {EMPTY, EMPTY, EMPTY, EMPTY};
unsigned int channel_enabled_count = 0;
unsigned int channel_enabled_status[MAX_CHANNEL_COUNT] = {0, 0, 0, 0};

volatile int transmission_error = 0;
volatile int conv_count_reached = 0;
volatile int measurement_activated = 0;

// -210 to 760°C
const uint8_t type_j_coefficients_count = 9;
const double type_j_coefficients[9] = {0,
									   5.0381187815 * pow(10, 1),
									   3.0475836930 * pow(10, -2),
									  -8.5681065720 * pow(10, -5),
									   1.3228195295 * pow(10, -7),
									  -1.7052958337 * pow(10, -10),
									   2.0948090697 * pow(10, -13),
									  -1.2538395336 * pow(10, -16),
									   1.5631725697 * pow(10, -20)

};

// -270 to 0°C
const uint8_t type_k_coefficients_count = 11;
const double type_k_coefficients[11] = {0,
										3.9450128025 * pow(10, 1),
										2.3622373598 * pow(10, -2),
									   -3.2858906784 * pow(10, -4),
									   -4.9904828777 * pow(10, -6),
									   -6.7509059173 * pow(10, -8),
									   -5.7410327428 * pow(10, -10),
									   -3.1088872894 * pow(10, -12),
									   -1.0451609365 * pow(10, -14),
									   -1.9889266878 * pow(10, -17),
									   -1.6322697486 * pow(10, -20)

};

// -270 to 0°C
const uint8_t type_t_coefficients_count = 15;
const double type_t_coefficients[15] = {0,
		 	 	 	 	 	 	 	 	3.8748106364 * pow(10, 1),
										4.4194434347 * pow(10, -2),
										1.1844323105 * pow(10, -4),
										2.0032973554 * pow(10, -5),
										9.0138019559 * pow(10, -7),
										2.2651156593 * pow(10, -8),
										3.6071154205 * pow(10, -10),
										3.8493939883 * pow(10, -12),
										2.8213521925 * pow(10, -14),
										1.4251594779 * pow(10, -16),
										4.8768662286 * pow(10, -19),
										1.0795539270 * pow(10, -21),
										1.3945027062 * pow(10, -24),
										7.9795153927 * pow(10, -28)
};

// -270 to 0°C
const uint8_t type_e_coefficients_count = 14;
const double type_e_coefficients[14] = {0,
										5.8665508708 * pow(10, 1),
										4.5410977124 * pow(10, -2),
									   -7.7998048686 * pow(10, -4),
									   -2.5800160843 * pow(10, -5),
									   -5.9452583057 * pow(10, -7),
									   -9.3214058667 * pow(10, -9),
									   -1.0287605534 * pow(10, -10),
									   -8.0370123621 * pow(10, -13),
									   -4.3979497391 * pow(10, -15),
									   -1.6414776355 * pow(10, -17),
									   -3.9673619516 * pow(10, -20),
									   -5.5827328721 * pow(10, -23),
									   -3.4657842013 * pow(10, -26)
};

/* USER CODE END PV */

/* Private function prototypes -----------------------------------------------*/
void SystemClock_Config(void);
static void MX_GPIO_Init(void);
static void MX_DMA_Init(void);
static void MX_ADC1_Init(void);
static void MX_ADC3_Init(void);
static void MX_ADC4_Init(void);
static void MX_TIM2_Init(void);
static void MX_I2C3_Init(void);
static void MX_DAC1_Init(void);
static void MX_ADC2_Init(void);
/* USER CODE BEGIN PFP */
int InterpretConfig(void);
int InterpretVariable(char name[CFG_VAR_SIZE], char value[CFG_VAR_SIZE]);
int SetupMeasurement(void);
int SendParameters(void);
float MeasureVref(void);
int StartMeasurement(void);
int SendData(enum ADC_BUFFER_STATE usb_transmition_state);
int SendTrasmissionReport(void);
int ResetStates(void);
/* USER CODE END PFP */

/* Private user code ---------------------------------------------------------*/
/* USER CODE BEGIN 0 */

/* USER CODE END 0 */

/**
  * @brief  The application entry point.
  * @retval int
  */
int main(void)
{
  /* USER CODE BEGIN 1 */

  /* USER CODE END 1 */

  /* MCU Configuration--------------------------------------------------------*/

  /* Reset of all peripherals, Initializes the Flash interface and the Systick. */
  HAL_Init();

  /* USER CODE BEGIN Init */

  /* USER CODE END Init */

  /* Configure the system clock */
  SystemClock_Config();

  /* USER CODE BEGIN SysInit */

  /* USER CODE END SysInit */

  /* Initialize all configured peripherals */
  MX_GPIO_Init();
  MX_DMA_Init();
  MX_ADC1_Init();
  MX_ADC3_Init();
  MX_ADC4_Init();
  MX_TIM2_Init();
  MX_USB_Device_Init();
  MX_I2C3_Init();
  MX_DAC1_Init();
  MX_ADC2_Init();
  /* USER CODE BEGIN 2 */
  ResetStates();

  int full_channels = 0;
  /* USER CODE END 2 */

  /* Infinite loop */
  /* USER CODE BEGIN WHILE */

  while (1)
  {
    /* USER CODE END WHILE */

    /* USER CODE BEGIN 3 */
	  if(prog_state == CFG_RECEIVED){
		  InterpretConfig();
	  }
	  if(prog_state == CFG_INTERPRETED){
		  SetupMeasurement();
	  }
	  if(prog_state == PARAMETERS_SET){
		  SendParameters();
	  }
	  if(prog_state == ARMED){
		  while(!measurement_activated);
		  StartMeasurement();
	  }
	  if(prog_state == MEASURING){
		 full_channels = 0;
		 for(int i = 0; i < MAX_CHANNEL_COUNT; i++){
			 if(!channel_enabled_status[i])
				 continue;
			 if(adc_states[i] == EMPTY)
				 break;

			 if(usb_transmition_state == EMPTY){
				 usb_transmition_state = adc_states[i];
			 }
			 else if(adc_states[i] != usb_transmition_state){
				 transmission_error = 1;
				 break;
			 }

			 full_channels++;
		 }

		 if(full_channels == channel_enabled_count){
			 SendData(usb_transmition_state);
			 usb_transmition_state = EMPTY;
		 }

		 if(current_packet_count >= target_packet_count) {
			 prog_state = REPORTING;
		 }
	  }
	  if(prog_state == REPORTING){
		  SendTrasmissionReport();
		  prog_state = DONE;
	  }
	  if(prog_state == DONE){

		  ResetStates();
	  }


  }
  /* USER CODE END 3 */
}

/**
  * @brief System Clock Configuration
  * @retval None
  */
void SystemClock_Config(void)
{
  RCC_OscInitTypeDef RCC_OscInitStruct = {0};
  RCC_ClkInitTypeDef RCC_ClkInitStruct = {0};

  /** Configure the main internal regulator output voltage
  */
  HAL_PWREx_ControlVoltageScaling(PWR_REGULATOR_VOLTAGE_SCALE1_BOOST);

  /** Initializes the RCC Oscillators according to the specified parameters
  * in the RCC_OscInitTypeDef structure.
  */
  RCC_OscInitStruct.OscillatorType = RCC_OSCILLATORTYPE_HSI48|RCC_OSCILLATORTYPE_HSE;
  RCC_OscInitStruct.HSEState = RCC_HSE_ON;
  RCC_OscInitStruct.HSI48State = RCC_HSI48_ON;
  RCC_OscInitStruct.PLL.PLLState = RCC_PLL_ON;
  RCC_OscInitStruct.PLL.PLLSource = RCC_PLLSOURCE_HSE;
  RCC_OscInitStruct.PLL.PLLM = RCC_PLLM_DIV2;
  RCC_OscInitStruct.PLL.PLLN = 78;
  RCC_OscInitStruct.PLL.PLLP = RCC_PLLP_DIV6;
  RCC_OscInitStruct.PLL.PLLQ = RCC_PLLQ_DIV2;
  RCC_OscInitStruct.PLL.PLLR = RCC_PLLR_DIV2;
  if (HAL_RCC_OscConfig(&RCC_OscInitStruct) != HAL_OK)
  {
    Error_Handler();
  }

  /** Initializes the CPU, AHB and APB buses clocks
  */
  RCC_ClkInitStruct.ClockType = RCC_CLOCKTYPE_HCLK|RCC_CLOCKTYPE_SYSCLK
                              |RCC_CLOCKTYPE_PCLK1|RCC_CLOCKTYPE_PCLK2;
  RCC_ClkInitStruct.SYSCLKSource = RCC_SYSCLKSOURCE_PLLCLK;
  RCC_ClkInitStruct.AHBCLKDivider = RCC_SYSCLK_DIV1;
  RCC_ClkInitStruct.APB1CLKDivider = RCC_HCLK_DIV1;
  RCC_ClkInitStruct.APB2CLKDivider = RCC_HCLK_DIV1;

  if (HAL_RCC_ClockConfig(&RCC_ClkInitStruct, FLASH_LATENCY_4) != HAL_OK)
  {
    Error_Handler();
  }
}
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

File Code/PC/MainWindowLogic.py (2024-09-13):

import math
import os
import threading
from datetime import datetime

import jsonpickle as jsonpickle
import serial
import serial.tools.list_ports
from PyQt5.QtCore import QRegularExpression, Qt, QSize
from PyQt5.QtGui import QColor, QIcon
from PyQt5.QtWidgets import *
from PyQt5.QtWidgets import QApplication
from send2trash import send2trash
from serial import SerialTimeoutException, SerialException

from MainWindowUI import Ui_Form
from MeasurementData.LogData import Record
import MeasurementData.Parameters as Parameters
from PlotWindowLogic import PlotLogic

from PyQt5 import QtWidgets, QtGui
import sys


class MainWindowLogic:

    def __init__(self):
        self.ui = Ui_Form()
        self.app = QtWidgets.QApplication(sys.argv)
        self.app.setWindowIcon(QtGui.QIcon("UI/icon.png"))
        self.app.aboutToQuit.connect(self.stop_serial_ports)
        self.form = QtWidgets.QWidget()
        self.current_folder = Parameters.record_folder_dir
        self.record = Record(number_of_channels=4)
        self.serial = None
        self.serial_gen = None
        self.connection_established = False
        self.connection_established_gen = False

        self.log_parameter_names = None
        self.log_data = None

        self.read_thread_gen = None
        self.read_thread_active = False

        self.waiting_for_trigger = False
        self.receiving_temp_data = False
        self.save_generator_log = False
        self.gen_log_received = False

    def run(self):
        self.ui.setupUi(self.form)
        self.form.setWindowTitle("High Speed Thermocouple Logger")
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

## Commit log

2024-03-11 Temperature prediction algorithm
2024-03-19 Initial EMI filter design simulation
2024-03-21 More changes to RF filter
2024-03-27 Added rejection filter for 1MHZ differential signals
2024-03-27 Reduced filter order and improved design
2024-04-03 Wrote the IC sensor chapter
2024-04-03 Wrote the thermocouple and temperature sensor comparison chapters
2024-04-11 Calculated and chose power supply and reference voltages, edited the EMI filter to use exact values
    [General_4L_35um_5KT.PcbDoc, General_4L_35um_5KT_PANEL.PcbDoc, Preamp_v1.0.kicad_pcb, Preamp_v1.0.kicad_sch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]
2024-04-15 Chose a power supply transformer and created footprint for it
    [44164.PcbLib, 44164.Schlib, 44237.PcbLib, 44237.Schlib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]
2024-04-17 Designed the in-amp +5V/-5V power supply
    [L7805AC.Schlib, L7905AC.Schlib, power.SchDoc]
2024-04-17 Designed the MCU +3.3V power supply
    [44200.PcbLib, 44200.Schlib, 44236.PcbLib, 44236.Schlib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]
2024-04-22 Designed the in-amp schematic and added a thermocouple connector footprint
    [AD8421BRZ.SchLib, PCC-SMD-1000.stp, SOIC127P600X175-8N(SOIC_8).PcbLib, TC_2PIN_FEMALE.SchLib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]
2024-04-23 Designed the capacitors for the 1MHz filter
    [49R9.Schlib, CTSC3S.PcbLib, CTSC3S.Schlib, Ferr-Inductor_Calc.xlsx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]
2024-04-24 Finished the design of the 1MHz filter
    [B65659F0001X023.step, B65808B2203X000.step, B65808E1508T001.step, C_376p667.SchDoc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]
2024-04-25 Started designing the MCU schematic
    [STM32G474RET6.SchLib, Top.SchDoc, cjc.SchDoc, high-speed-thermocouple-logger.PrjPcb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]
2024-04-26 Added reverse polarity protection to the in-amp output (precision rectifier circuit)
    [inamp.SchDoc, mcu.SchDoc]
2024-04-29 Made some changes to the precision rectifier circuit
    [inamp.SchDoc, mcu.SchDoc]
2024-04-30 Finished the initial version of the schematic (one channel)
    [C_376p667.SchDoc, C_76p593.SchDoc, ProjectInfo.SchDoc, Top.SchDoc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]
2024-05-09 Made some small changes to the schematic and added an additional sheet for external connections (USB and trigger switches)
    [C_376p667.SchDoc, C_76p593.SchDoc, ProjectInfo.SchDoc, RM6.PcbLib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]
2024-05-09 Renamed the PCB files
    [high-speed-thermocouple-logger.PrjPcb, high-spped-thermocouple-logger.PcbDoc, high-spped-thermocouple-logger_panel.PcbDoc]
2024-05-10 Initial placement of the power block components
    [ProjectInfo.SchDoc, RM6.PcbLib, high-speed-thermocouple-logger.PrjPcb, power.SchDoc]
2024-05-13 Initial placement of the MCU and filter block components
    [RM6.PcbLib, SSW-104-02-T-S-RA.PcbLib, SSW-104-02-T-S-RA.Schlib, SSW-104-02-T-S-RA.stp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]
2024-05-14 Initial placement of all components, started fixing silkscreen
    [cjc.SchDoc, external.SchDoc, filter.SchDoc, inamp.SchDoc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]
2024-05-15 Finished the initial placement of the silkscreen and moved some components
    [ProjectInfo.SchDoc, filter.SchDoc]
2024-05-16 Routed most of the board
    [RM6.PcbLib, power.SchDoc]
2024-05-17 Routed most of the power nets
    [external.SchDoc, mcu.SchDoc]
2024-05-20 Finished routing the power nets, routed the MCU GND
2024-05-21 Finished routing the whole board (one channel only)
    [CTSC3S.PcbLib, ProjectInfo.SchDoc]
2024-05-22 Added and routed the rest of the channels
    [ProjectInfo.SchDoc, Top.SchDoc, high-speed-thermocouple-logger.PrjPcb, inamp.SchDoc]
2024-05-28 Made multiple changes to the schematic and PCB according to design reviews
    [Top.SchDoc, filter.SchDoc, inamp.SchDoc, mcu.SchDoc]
2024-05-29 Finished up the board with all of the design review changes
    [high-speed-thermocouple-logger.PrjPcb, high-spped-thermocouple-logger_panel.PcbDoc]
2024-05-30 Finalized the initial version of the board and prepared it for manufacturing
    [54R9.Schlib, Top.SchDoc, high-speed-thermocouple-logger.PrjPcb, high-spped-thermocouple-logger_panel.PcbDoc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]
2024-06-03 Last minute fixes before ordering the boards; Made a 2 channel version of the PCB
    [ProjectInfo.SchDoc, TC_PCC-SMD.PcbLib, high-speed-thermocouple-logger.PrjPcb, high-spped-thermocouple-logger-2ch_panel.PcbDoc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]
2024-06-04 Fixed an error in the production info table
    [high-spped-thermocouple-logger_panel.PcbDoc]
2024-06-06 Added more UI functionality and made a sample data .json
2024-06-07 Added plotting functionality (data filtering, predicted curve generation, predicted curve filtering)
2024-06-12 Fixed signal names in the schematics and edited the documentation in accordance with the review
    [Top.SchDoc, filter.SchDoc, inamp.SchDoc, mcu.SchDoc]
2024-06-12 Made an alternate version of the schematic for use in the documentation, wrote the Block scheme chapter
    [C_376p667.SchDoc, C_76p593.SchDoc, ProjectInfo.SchDoc, Top.SchDoc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]
2024-06-13 Wrote the Power supply design chapter
    [Top.SchDoc, mcu.SchDoc, power.SchDoc]
2024-06-14 Wrote the Filter design chapter
    [filter.SchDoc, inamp.SchDoc]
2024-06-15 Wrote the Amplification design chapter
    [inamp.SchDoc]
2024-06-16 Rearranged the MCU schematic
    [mcu.SchDoc]
2024-06-19 Initial version of the MCU code working with the real device
2024-06-20 Cold junction compensation, measurement parameters transfer to PC
    [cjc.SchDoc]
2024-06-21 Added measurement activation triggering, fixed temperature prediction, fixed some bugs with data transfer to PC, added filter measurements
2024-06-21 Made sample measurements
2024-06-22 Took images of the UI and sample measurements, copied the documents for the annexes
    [power.SchDoc]
2024-06-22 Added PCB 3D image
2024-06-22 Made code block schemes, wrote the PCB chapter
2024-06-23 Added a documentation .pdf file with attached annexes
2024-06-25 Added more documents and made some changes to the documentation
    [power.SchDoc]
2024-06-26 Replaced some elements in the schematic, improved the UI and fixed some bugs with transmitting non-full ADC buffers
    [power.SchDoc]
2024-07-16 Added Vref+ and DAC calibration procedures
2024-07-29 Added generator communication to the PC application
    [high-speed-thermocouple-logger.PrjPcb]
2024-08-20 Added a script that plots temperature as a function of generator parameters and changed the plotting library for the scripts to plotly
2024-08-21 Added a script that calculates predicted temperature for select logs and added a script that plots Tmax@W = f(S)

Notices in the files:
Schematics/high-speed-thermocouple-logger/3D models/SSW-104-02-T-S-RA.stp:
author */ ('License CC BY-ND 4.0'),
